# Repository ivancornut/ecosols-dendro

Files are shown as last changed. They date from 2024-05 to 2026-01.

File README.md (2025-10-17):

# Fine Open Dendro
A point dendrometer for small trunks and branches of tropical trees



## Objectives
Build a high precision point dendrometer to daily variations in water status and seasonnal growth of trees. 
There are already designs for point dendrometers on the market. Unfortunately most of them are based on a screw design and their linearity is sub-par or use very expensive LVDTs (100s of €). We choose to overcome these issues by inspiring ourselves on previous designs that use rods ([PepiPiaf](https://piaf.clermont.hub.inrae.fr/methodes-et-modeles/pepipiaf)) and by selecting high quality linear potentiometers instead (less than 50€).

## Hardware
### Mechanics
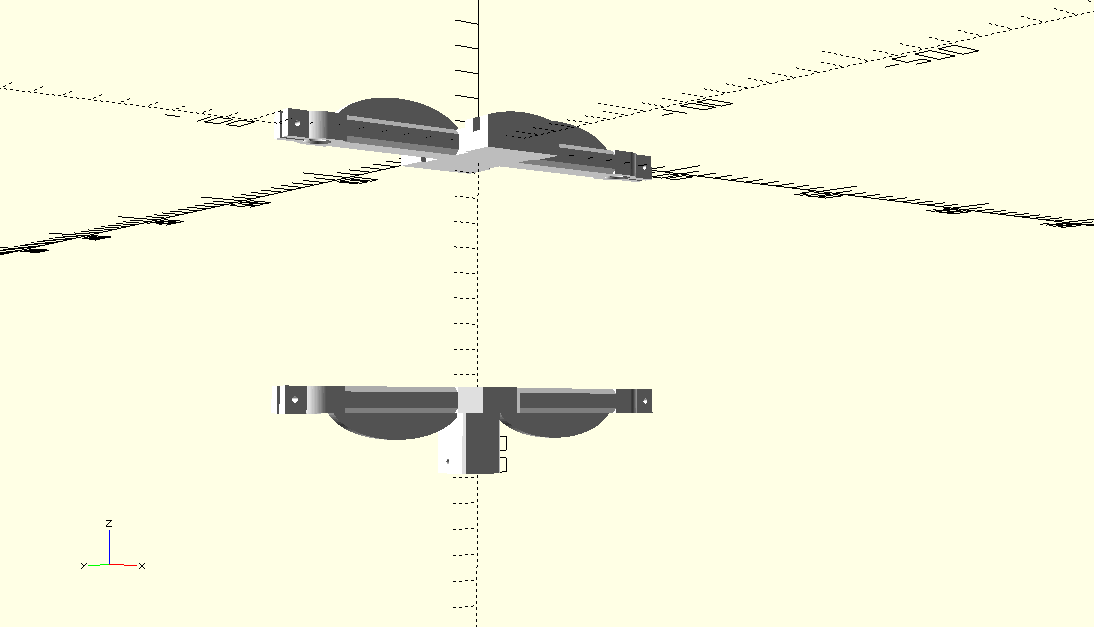
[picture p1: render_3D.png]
Render of dendrometer


The build is based on a 3D printed holder and carbon-fiber rods. The 3D printed holder gives us the ease of fabrication, ease of prototyping and low-cost that makes it possible to build a large number of said dendrometers for a reasonnable price. They also make the design easily upgradeable with feedback from users. The carbon-fiber rods give us a good temperature response of the dendrometer due to their low expansion coefficient.

The branch/trunk holder and lvdt holder 3D models are generated using [OpenScad](https://openscad.org/) and the [BOSL2](https://github.com/BelfrySCAD/BOSL2) library. The scripts can be found in the openscad-files folder. Openscad is an open-source software can be installed on any operating system. This means that the holders are parametrisable to your own case. This means you can adapt the model to the branch/truk diameter of your use case. This is a big adavantage of 3D printed holders. Once you have generated the 3D models you can export the STL files. 

The holders are meant to be printed in glass fiber PETG filament at 0.25mm layer height with a 0.6mm nozzle. The filament is the [Nanovia GF-UV PETG](https://nanovia.tech/en/ref/nanovia-petg-gf-uv/). The designs here were printed using a Prusa Mk4 and by drying the filament at 60°C for 12h (important !).

### Electronics
#### Linear potentiometer
The linear potentiometer that we use has a stated 0.5% linearity (is usually better in practice) and includes the spring (assuring contact) inside its body. It comes in a practical package around which the 3D printed holder is designed. The reference is BT404 and it can be found [here](https://www.mouser.fr/ProductDetail/858-404R10KL.5).
#### ADC
To read the output of the linear potentiometer we use the ADS1115 ADC. It has 16 bit precision that allows us to have a resolution of around 0.2µm (12.7mm of travel divided by 16 bits). This is of course overkill but a resolution of 1µm is useful when follwoing intra-daily varaitions of stem diameter.
#### Micro-controller
To read the ADC outputs we use a Pi-Pico running micropython. This is meant to be interfaceable with our own brand of ModBus network that we developped for instrumented sites (see [here](https://github.com/ivancornut/ecophys-modbus)).

## Calibration
### Fast Calibration of the linear potentiometer
To fast-calibrate the linearpotentiometer sensor we use a caliper and a small code that reads the outputs of the ADC connected to the linear potentiometer. The procedures, codes and example datasets to do this operation cab be found in the [/Calibration](/Calibration) folder. 
The picture below shows an example of caliper values versus ADC outputs:

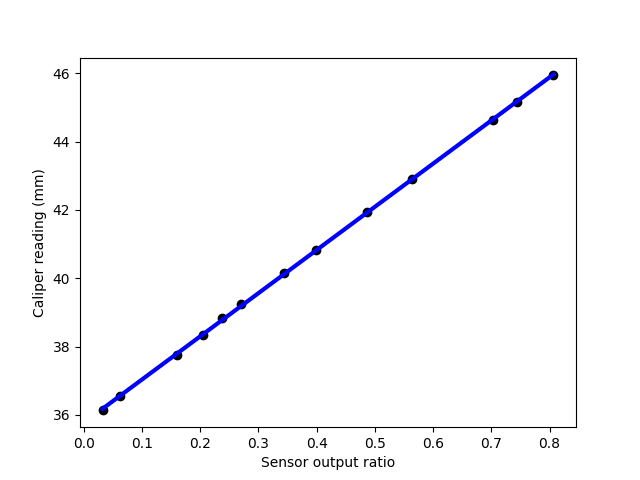
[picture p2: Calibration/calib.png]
calibration
. 

### Temperature response of the dendrometer
For calibration we use an aluminium rod with a known thermal expansion coefficient in a heating oven. By heating the whole setup we are able to calculate the deviation of the sensor due to thermal effects and calculate a linear correction to apply in the field. The code can be found [here](/Calibration_temp/calibration_temperature.ipynb). 
The graph below is the results when using our first prototype of the device:

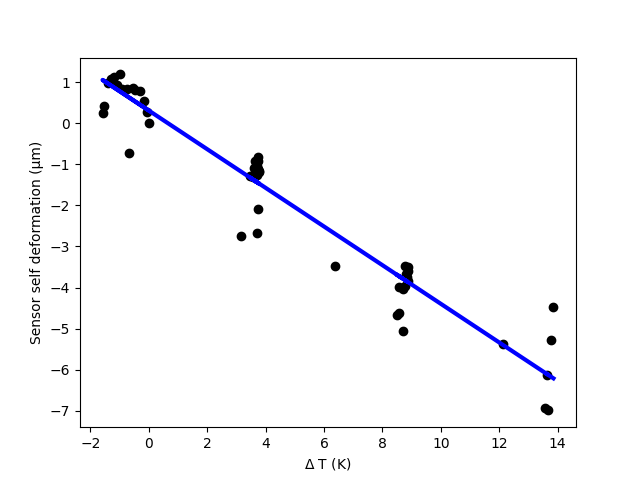
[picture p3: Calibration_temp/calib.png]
temperature calibration
.

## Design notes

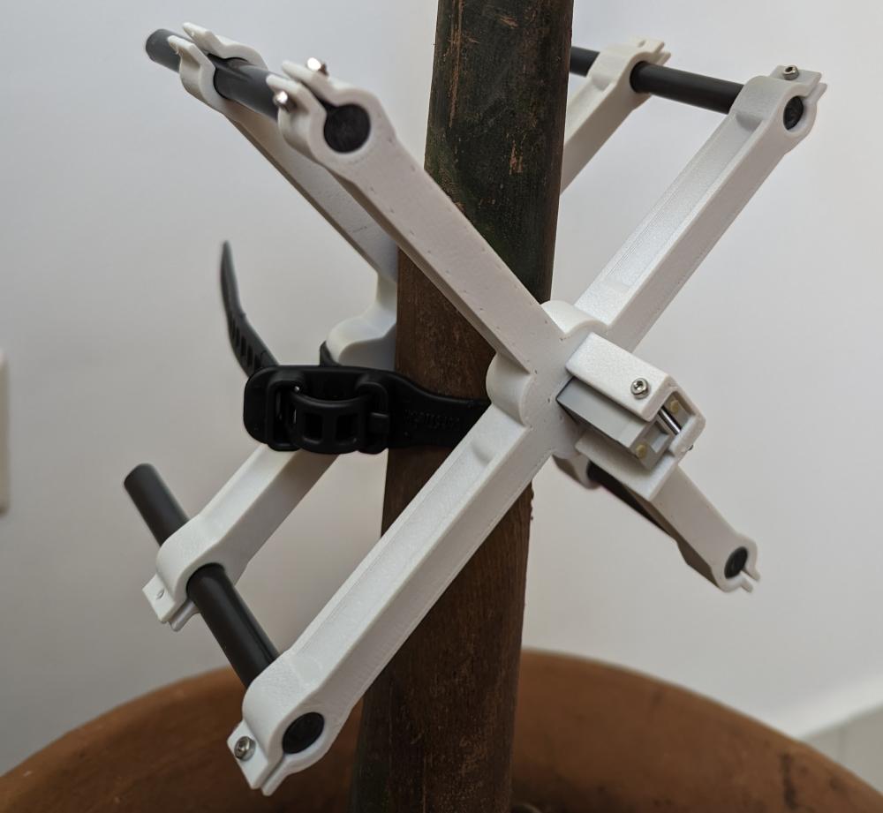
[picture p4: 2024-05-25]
dendro.jpg

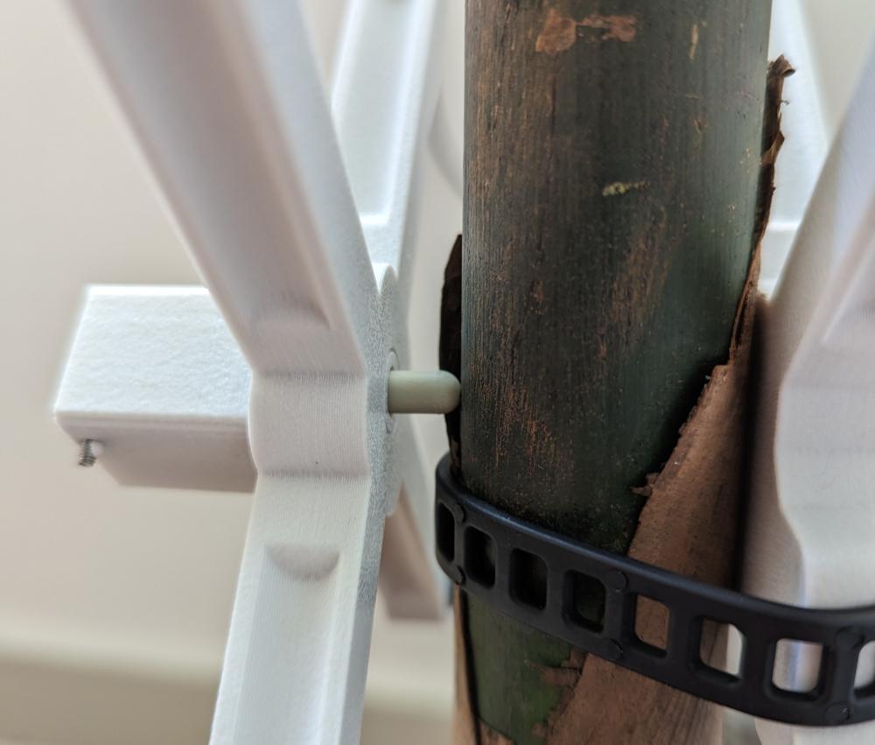
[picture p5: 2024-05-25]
cloesup_lvdt.jpg

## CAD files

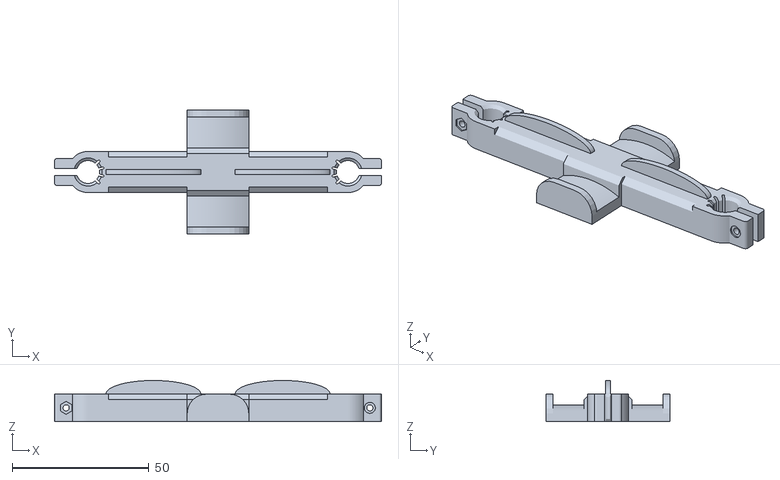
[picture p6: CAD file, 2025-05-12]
Example_stls/dendro_holder_part_05cm_diameter.stl
119.5 x 45.3 x 15.0

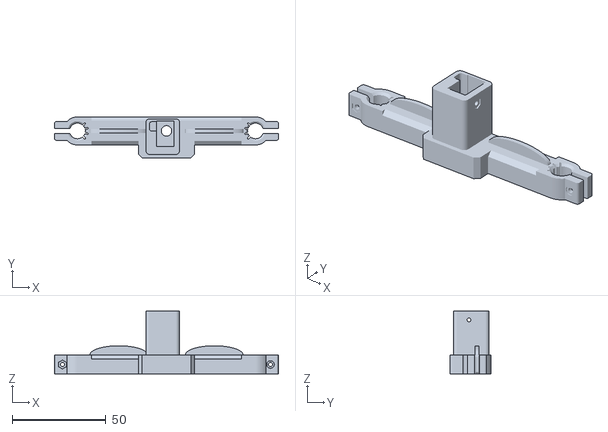
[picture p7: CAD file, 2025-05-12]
Example_stls/dendro_lvdt_part_05cm_diameter.stl
119.5 x 22.0 x 33.5

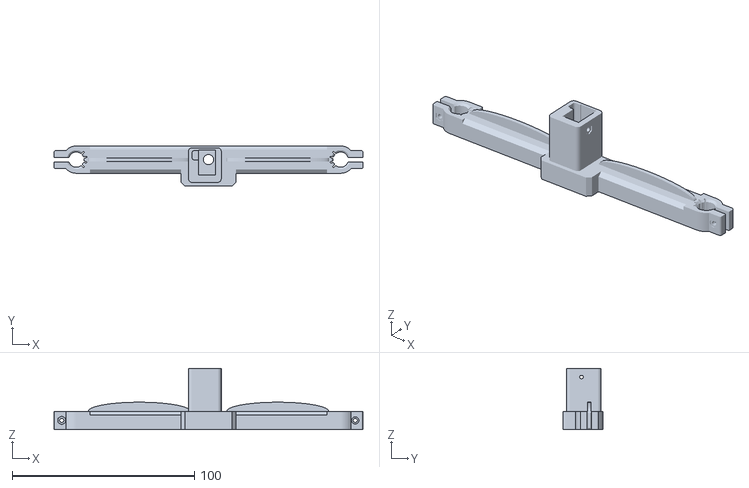
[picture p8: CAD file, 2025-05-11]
Example_stls/dendro_lvdt_part_10cm_diameter.stl
169.5 x 22.0 x 33.5

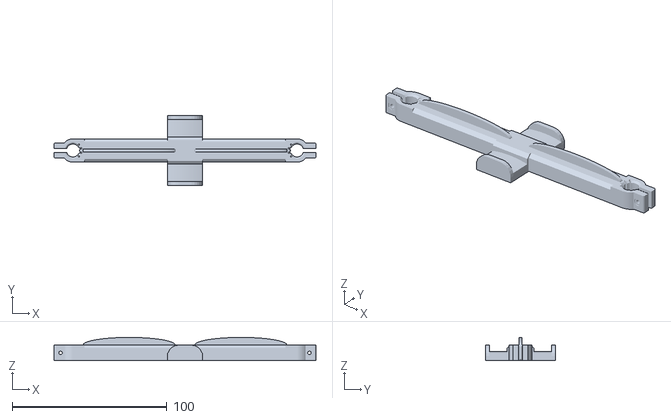
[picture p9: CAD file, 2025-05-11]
Example_stls/dendrometer_holder.stl
169.5 x 45.3 x 15.0

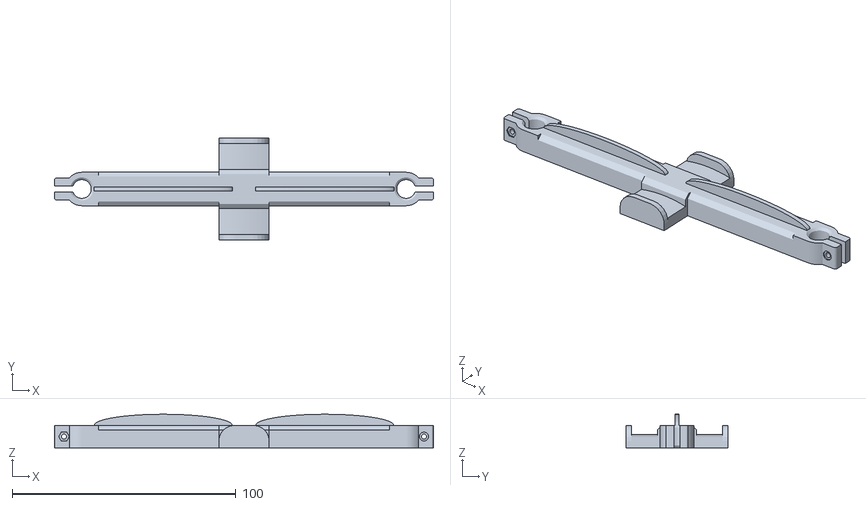
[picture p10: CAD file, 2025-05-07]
Example_stls/dendro_holder_part_10cm_diameter.stl
169.5 x 45.5 x 15.0

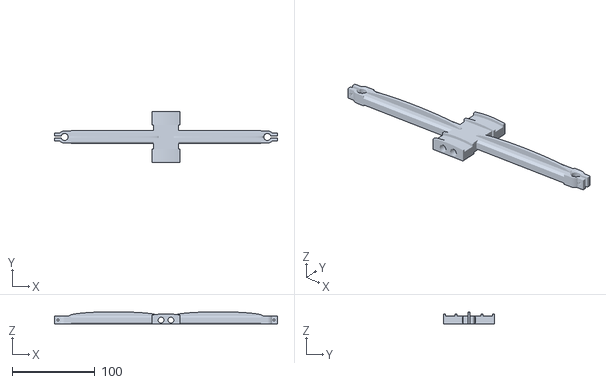
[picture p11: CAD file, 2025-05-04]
Example_stls/dendro_holder_part_20cm_diameter.stl
269.5 x 61.5 x 15.0

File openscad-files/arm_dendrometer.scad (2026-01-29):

include <BOSL2/std.scad>
include <flex_cuts.scad>


module dendro_arm(offset_arm, rot_angle,height,l){
    length_arm = l;
    width_arm = 15 ;
    height_arm = height ;

    c_tube_diam = 8 ;
    tube_holder_width = 3.5;
    tube_slack = 0.35;

    tube_tight_l = 6; 
    tube_tight_w = 10;
    tube_holder_diam = c_tube_diam + tube_holder_width*2;
    screw_diam = 2;
    tight_screw_offset = tube_holder_diam/2 +0.5;
    //translate([])
    color("white")
    rotate([0,0,rot_angle]){
        translate([length_arm/2+offset_arm,0,0]){
            union(){
                difference(){
                    // the arm of the holder
                    cuboid([length_arm,width_arm,height_arm], chamfer = 2, edges = [TOP+FRONT,TOP+BACK],$fn = 100);
                    rotate([0,90,0]){
                        cylinder(d = 6, h = length_arm-10,center = true,$fn = 100);
                    }
                }
                translate([length_arm/2+tube_holder_diam/2,0,0]){
                    difference(){
                        union(){
                            translate([-tube_holder_diam/4,0,0]){
                                cuboid([tube_holder_diam/2,tube_holder_diam,height_arm]);
                             }
                             cylinder(d = tube_holder_diam, h = height_arm, center = true,$fn=100);
                             translate([tube_holder_diam/2,0,0]){
                                // the cube to tighten the carbon fiber tube
                                cuboid([tube_holder_width+tube_tight_l,tube_tight_w,height_arm],
                                 rounding=1,edges=[RIGHT+FRONT, RIGHT+BACK],$fn=100);
                             } 
                        }
                        // the hole for the tube to fit in
                        cyl(d = c_tube_diam+tube_slack, h = height_arm+0.1,chamfer = -1,$fn=100);
                        cuts_flex(4,55,-55,c_tube_diam,2.5,height_arm+0.1,0.8);
                        translate([tube_holder_diam/2,0,0]){
                            // hole between the two parts that tighten
                            cube([tube_holder_width+tube_tight_l+0.1,2.5,height_arm+0.1], center = true);
                        }
                        translate([tight_screw_offset,0,0]){
                            rotate([90,0,0]){
                                // the hole for the tightening screw
                                cylinder(d = screw_diam+0.25,h = tube_holder_diam+2, center = true,$fn=100);
                                translate([0,0,tube_tight_w/2]){
                                    cylinder(d = 4,h=1,center = true,$fn=100);
                                }
                                translate([0,0,-(tube_tight_w/2)]){
                                    rotate([0,0,30]){
                                        regular_prism(n=6,od = 4.75,h=1,center = true);
                                    }
                                }
                            }                       
                        }                  
                    }
                }
                attachment = 6;
                length_ellipse = length_arm + attachment;
                width_ellipse = width_arm-12;
                translate([-2,-(width_ellipse)/2,height_arm/2]){
                    rotate([-90,0,0]){
                        linear_extrude(width_ellipse){
                            difference(){
                                ellipse(d=[length_ellipse,15],$fn=100);
                                translate([-length_ellipse/2-1,0,0]){
                                    square([length_ellipse+3,15]);
                                }
                            }
                        }
                    }
                }
            }
        }
    }

}

//dendro_arm(0,0,10,50);
//width_arm = 16;
//length_arm = 50;
//attachment = 10;
//length_ellipse = length_arm + attachment;
//width_ellipse = width_arm-14;
//translate([-2,-(width_ellipse)/2,10/2]){
//   rotate([-90,0,0]){
//   linear_extrude(width_ellipse){
//        difference(){
//            ellipse(d=[length_ellipse,10],$fn=100);
//                translate([-length_ellipse/2-1,0,0]){
//                    square([length_ellipse+3,20]);
//                }
//        }
//    }
//    }
//}

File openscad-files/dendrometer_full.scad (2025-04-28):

include <dendrometer_holder.scad>
include <dendrometer_lvdt.scad>

diameter_tree = 100;
nb_arms = 2;
width_dendro_center = 30;

dendrometer_holder(nb_arms,width_dendro_center,10,diameter_tree/2);
translate([0,0,-diameter_tree]){
    rotate([180,0,0]){
        dendrometer_lvdt(nb_arms,width_dendro_center,10,diameter_tree/2);
    }
}

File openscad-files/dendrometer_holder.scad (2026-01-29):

include <BOSL2/std.scad>
include <arm_dendrometer.scad>
include <lvdt404.scad>
include <holder.scad>

nb_arms_dendro = 2;
width_holder = 22.5; // should not be changed usually
tree_trunk_width = 120; // adapt to your tree
holder_arms_length = tree_trunk_width/2 - (width_holder-30)/2 ;
height_arms_and_holder = 10; // this will affect the rigidity, 10 is a good compromise

module dendrometer_holder(nb_arms,width, height, arm_length,tree_width){
    ziptie_width = 11.5;
    color("white")
    //difference(){
        union(){
        // the main body of the structure
            cuboid([width,width-5,height], chamfer = 2, edges = [TOP+FRONT,TOP+BACK]);
            if(nb_arms>0){
                dendro_arm(offset_arm = width/2,rot_angle = 0, height = height, l = arm_length);
                if(nb_arms==4) dendro_arm(offset_arm = width/2,rot_angle = 90, height = height, l = arm_length);
                dendro_arm(offset_arm = width/2,rot_angle = 180, height = height, l = arm_length);
                if(nb_arms>2) dendro_arm(offset_arm = width/2,rot_angle = 270, height = height, l = arm_length);
            }
            // The two holders for the flexible zip-ties
            translate([0,-((width-5)+ziptie_width)/2+0.1,-height/2]){
                holder(ziptie_width,height,tree_width,width);
                }
            translate([0,+((width-5)+ziptie_width)/2-0.1,-height/2]){
                rotate([0,0,180]){
                    holder(ziptie_width,height,tree_width,width);
                }
            }
        }
        // Following are the holes that make the dendrometer consume less plastic and more rigid
        //rotate([90,0,0]){
        //    translate([-6,0,0]){
        //        cylinder(d = 7,h=,center = true,$fn = 100);
        //    }
        //    translate([6,0,0]){
        //        cylinder(d = 7,h=0,center = true,$fn = 100);
        //    }
        //}
    //}
}
dendrometer_holder(nb_arms_dendro,width_holder,height_arms_and_holder,holder_arms_length,tree_trunk_width);

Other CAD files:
openscad-files/dendrometer_lvdt.scad
openscad-files/flex_cuts.scad
openscad-files/holder.scad
openscad-files/lvdt404.scad
openscad-files/water_evac.scad

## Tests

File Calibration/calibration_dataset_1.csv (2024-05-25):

Ratio | Disp
0.8066986 | 45.96
0.7437 | 45.16
0.702931 | 44.64
0.5645233 | 42.9
0.4871258 | 41.93
0.3982297 | 40.82
0.3444886 | 40.14
0.2702549 | 39.24
0.2366453 | 38.84
0.204236 | 38.33
0.1599097 | 37.76
0.06226059 | 36.54
0.03233126 | 36.13

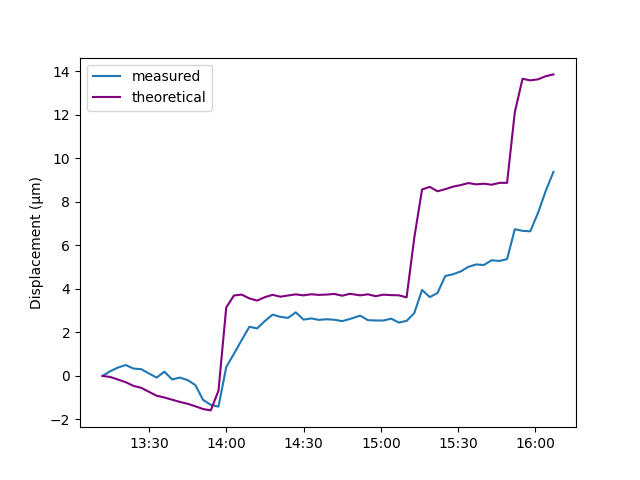
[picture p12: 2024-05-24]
Calibration_temp/Dendro.png

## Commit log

2024-05-22 Added stl for part that attaches to tree
    [Tree attach.stl]
2024-05-24 Add stls and render
    [LVDT_holder_part.stl]
2024-05-24 Add temperature calibration
2024-05-25 Add calibration code and example dataset
    [calibration_dataset_1.csv]
2025-04-27 Added openscad files
    [arm_dendrometer.scad, dendrometer_lvdt.scad, lvdt404.scad]
2025-04-28 Small changes
    [dendrometer_lvdt.scad, lvdt404.scad]
2025-04-28 Creation of dendrometer holder
    [dendrometer_full.scad, dendrometer_holder.scad, dendrometer_lvdt.scad, holder.scad]
2025-04-28 Small bugs
    [dendrometer_holder.scad, dendrometer_lvdt.scad, holder.scad]
2025-05-01 Changes to the tightening screw design
    [arm_dendrometer.scad]
2025-05-02 Improving stiffness and decreasing weight
    [arm_dendrometer.scad, dendrometer_holder.scad]
2025-05-02 minor changes to openscad files
    [dendrometer_holder.scad, dendrometer_lvdt.scad]
2025-05-03 Small changes to design
    [dendrometer_holder.scad, dendrometer_lvdt.scad, lvdt404.scad]
2025-05-03 Added small water evacuation channel
    [dendrometer_lvdt.scad, water_evac.scad]
2025-05-04 Added stls files for common tree diameters
    [LVDT_holder_part.stl, Tree attach.stl, dendro_holder_part_05cm_diameter.stl, dendro_holder_part_10cm_diameter.stl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]
2025-05-06 Major changes to design to reduce material cost and increase ease of printing
    [arm_dendrometer.scad, dendro_holder_part_10cm_diameter.stl, dendrometer_holder.scad, dendrometer_lvdt.scad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]
2025-05-11 Made the carbon tube holder a bit flexible
    [arm_dendrometer.scad, dendro_lvdt_part_10cm_diameter.stl, dendrometer_holder.scad, dendrometer_holder.stl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]
2025-09-15 Small improvements to 3D design
    [dendrometer_holder.scad, dendrometer_lvdt.scad, lvdt404.scad]
2026-01-29 Repair small bugs in LVDT insertion in design
    [arm_dendrometer.scad, dendrometer_holder.scad, dendrometer_lvdt.scad, lvdt404.scad]
